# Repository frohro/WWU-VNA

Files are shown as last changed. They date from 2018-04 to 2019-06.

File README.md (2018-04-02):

# WWU-VNA
An Inexpensive Vector Network Analyzer Project for the Walla Walla University Electronics II Class

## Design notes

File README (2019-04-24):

This is some source code for the WWU VNA.  The hardware files can be found at this repository:  
https://github.com/frohro/WWU-VNA

These instructions were done an a Ubuntu Linux computer.  They will vary slightly for Windows or OS X.

Build Instructions:

	- git clone the repository.  
	- Install Code Composer Studio. (This works with CCS 8.2 and 9.0.) 
		- You need the MSP432 Red board library version 5.23.1 or later or you will have build errors.
	- Install Energia, and using Energia's Tools->Boards:->Boards Manager, add the MSP432P401P (red board)
	- Energia uses the Arduino way of handling libraries, and it is easiest to use that as well, because
		CCS knows how to import things better that way.  So in your ~/Energia/libraries folder make 
		folders for each of the libraries.  Mine look like this.
		:~/Energia$ ls -lah libraries
		total 36K
		drwxr-xr-x 8 frohro frohro 4.0K Apr 15 21:07 .
		drwxr-xr-x 5 frohro frohro 4.0K Apr  5 14:30 ..
		drwxr-xr-x 2 frohro frohro 4.0K Apr 21 21:29 adc14vna
		drwxr-xr-x 2 frohro frohro 4.0K Apr 15 21:15 constants
		drwxr-xr-x 2 frohro frohro 4.0K Apr  5 14:33 DynamicCommandParser
		-rw-r--r-- 1 frohro frohro   88 Oct 11  2018 readme.txt
		drwxr-xr-x 2 frohro frohro 4.0K Apr 21 21:31 si5351
		drwxr-xr-x 2 frohro frohro 4.0K Apr 21 21:30 SignalProcessing
		
		Inside those make symbolic links to the appropriate files in your git repository.
		For example, 

	- Import Energia Sketch using File->Import...->Energia->Energia Sketch.
	- Be sure to select MSP432P401R as the processor.
	- Right click on the project, and select add files.
		- Add the .cpp, .c, and .h files.
	- Click the hammer to build in CCS.

	- Under languages, select C11 and c++17
	- Under Build Settings->Miscellaneous->Miscellaneous C++ source specific flags add -fpermissive.

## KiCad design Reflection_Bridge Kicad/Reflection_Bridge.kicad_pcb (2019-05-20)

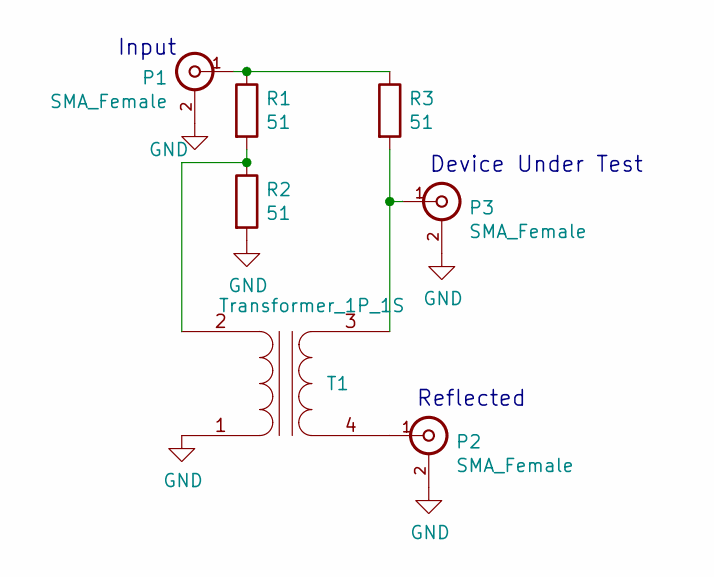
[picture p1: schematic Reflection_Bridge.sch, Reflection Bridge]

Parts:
P1, P2, P3: SMA_Female; SMA_EDGE
R1, R2, R3: 51; R_0805
T1: Transformer_1P_1S; 1_to_1_Balun

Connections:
GND: P1.2 (Ext), P2.2 (Ext), P3.2 (Ext), R2.2, T1.1 (AA)
unnamed: P1.1 (In), R1.1, R3.1
unnamed: P2.1 (In), T1.4 (SB)
unnamed: P3.1 (In), R3.2, T1.3 (SA)
unnamed: R1.2, R2.1, T1.2 (AB)

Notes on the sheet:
Input
Device Under Test
Reflected

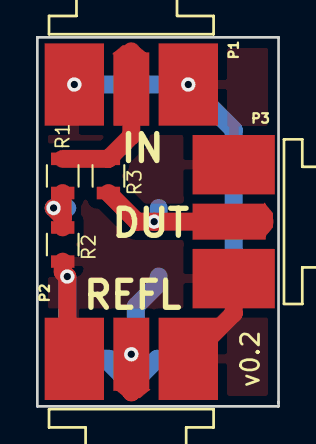
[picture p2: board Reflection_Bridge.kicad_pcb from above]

Board: 2 copper layers, 13.4 x 20.5 mm, 7 parts (1 on the bottom side), 5 nets.

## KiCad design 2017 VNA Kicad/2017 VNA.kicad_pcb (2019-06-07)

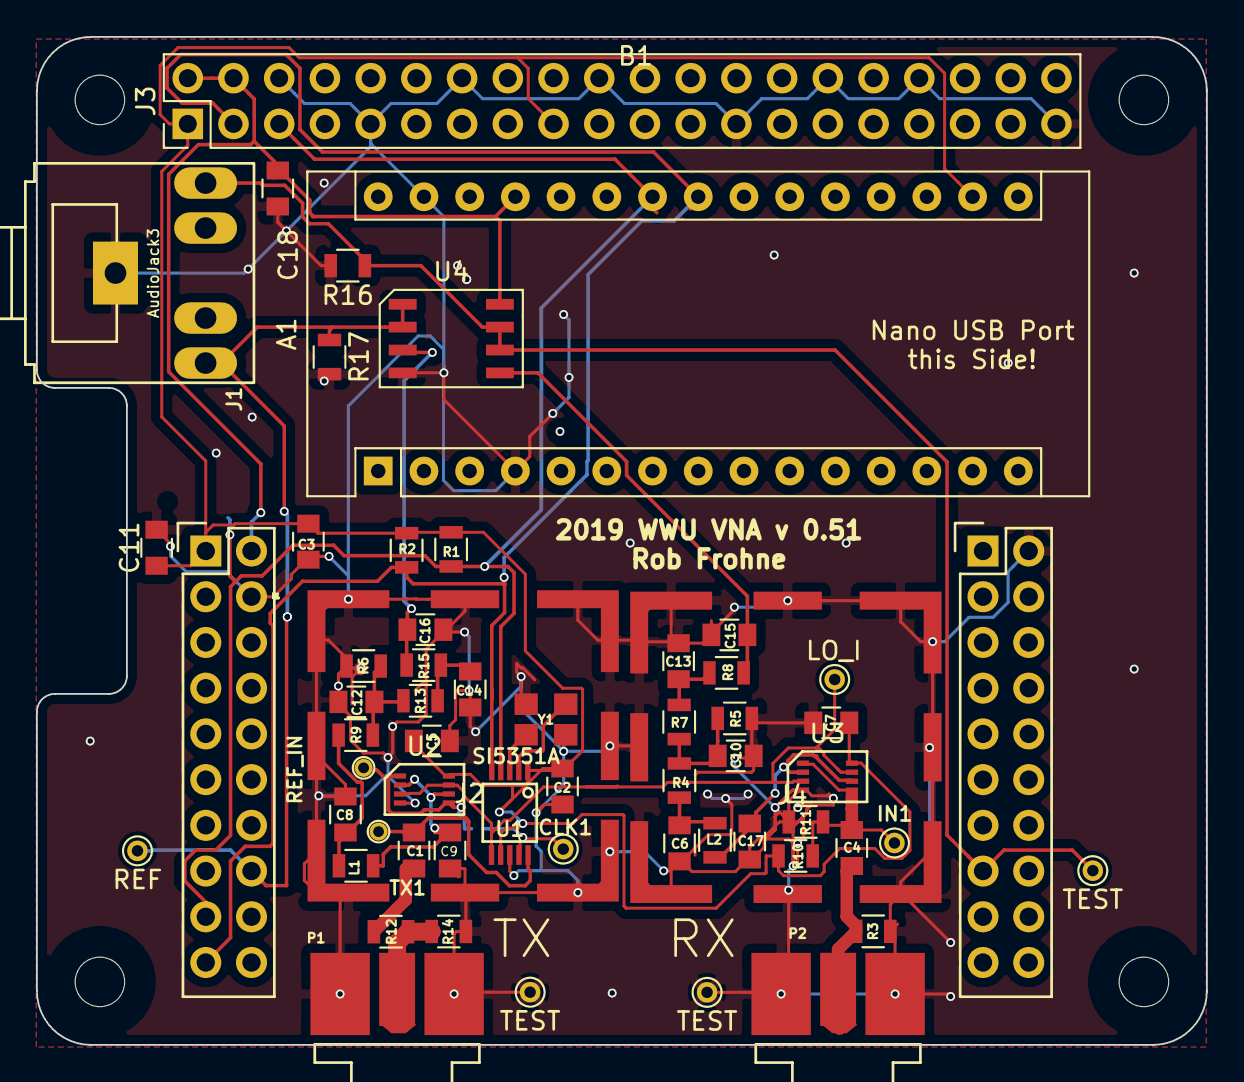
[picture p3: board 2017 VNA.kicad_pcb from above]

Board: 2 copper layers, 65.0 x 56.0 mm, 60 parts (1 on the bottom side), 27 nets.

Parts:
A1: Arduino_Nano_v3.x; Arduino_Nano
B1: EXP-_MSP432P401R_BoosterPack; TI_BoosterPack
C1, C4: 1.0uF; C_0805
C2: .1uf; C_0805
C3: 10uF; C_0805
C5, C7: .1uF; C_0805
C6, C8: 680nF; C_0805
C9, C17: .005uF; C_0805
C10, C12: 10nF; C_0805
C11, C18: 0.1uF; C_0805
C13, C14, C15, C16: 1nF; C_0805
CLK1: LO_Q; PINTST
GND1, GND2: TEST; PINTST
IN1: IN; PINTST
J1: AudioJack3; Tayda_3.5mm_stereo_TRS_jack_A-853
J2, J4: RF_Shield_Two_Pieces; LAIRD-BMI-S-202
J3: Raspberry_Pi_2_3; Pin_Header_Straight_2x20_Pitch2.54mm
JP1: Jumper; SOLDER_JUMPER
L1, L2: 100uH; L_0805
LO_I1: LO_I; PINTST
P1: Output; SMA_EDGE
P2: Input; SMA_EDGE
R1, R2: 4.7k; R_0805
R3: 47; R_0805
R4, R9: 10k; R_0805
R5, R6: 30k; R_0805
R7, R13: 51k; R_0805
R8, R15: 1M; R_0805
R10: 39K; R_0805
R11: 220K; R_0805
R12, R14: R; R_0805
R16, R17: 180; R_0805
TP1: REF_IN; PINTST
TP2: REF; PINTST
TP3: TEST; PINTST
TX1: LO_Q; PINTST
U1: SI5351A; MSOP-10
U2, U3: NL7WB66; VFSOP-8
U4: LM2904; SOIC-8
Y1: CX3225

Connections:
+3V3: A1.17, B1.3.3V, C2.2, C3.1, C5.2, C7.1, C11.1, J3.1, J3.17, R1.2, R2.2, R10.1, U1.1, U1.7, U2.8, U3.8
+5V: A1.27, B1.5V, C18.1, J3.2, J3.4, U4.8
/LO_I: LO_I1.1, U1.6, U2.3, U2.7, U3.3, U3.7
/Ref_In: JP1.2, TP1.1, U2.1, U2.5
/SCL: A1.24, B1.P6.5, J3.5, R1.1, U1.4
/SDA: A1.23, B1.P6.4, J3.3, R2.1, U1.5
/TX: C1.2, TX1.1, U1.10
/Test_In: C4.1, IN1.1, R10.2, R11.1, U3.1, U3.5
GND: A1.4, A1.29, B1.GND, B1.GND1, C2.1, C3.2, C5.1, C6.2, C7.2, C8.2, C9.2, C10.2, C11.2, C12.2, C13.2, C14.2, C15.2, C16.2, C17.2, C18.2, GND1.1, GND2.1, J1.1, J2.1, J3.6, J3.9, J3.14, J3.20, J3.25, J3.30, J3.34, J3.39, J4.1, P1.2, P2.2, R3.2, R5.2, R6.2, R11.2, R14.1, R16.2, R17.2, U1.8, U2.4, U3.4, U4.4, Y1.2, Y1.4
unnamed: B1.P4.7, J1.3, R17.1, TP2.1, U4.1, U4.2
unnamed: B1.P5.1, J1.2, R16.1, TP3.1, U4.6, U4.7
unnamed: C1.1, R12.2
unnamed: C4.2, P2.1, R3.1
unnamed: C6.1, L2.2, R4.2
unnamed: C8.1, L1.2, R9.2
unnamed: C9.1, L1.1, U2.2, U2.6
unnamed: C10.1, R4.1, R5.1, R7.2
unnamed: C12.1, R6.1, R9.1, R13.2
unnamed: C13.1, R7.1, R8.2
unnamed: C14.1, R13.1, R15.2
unnamed: C15.1, R8.1, U4.5
unnamed: C16.1, R15.1, U4.3
unnamed: C17.1, L2.1, U3.2, U3.6
unnamed: CLK1.1, JP1.1, U1.9
unnamed: P1.1, R12.1, R14.2
unnamed: U1.2, Y1.1
unnamed: U1.3, Y1.3

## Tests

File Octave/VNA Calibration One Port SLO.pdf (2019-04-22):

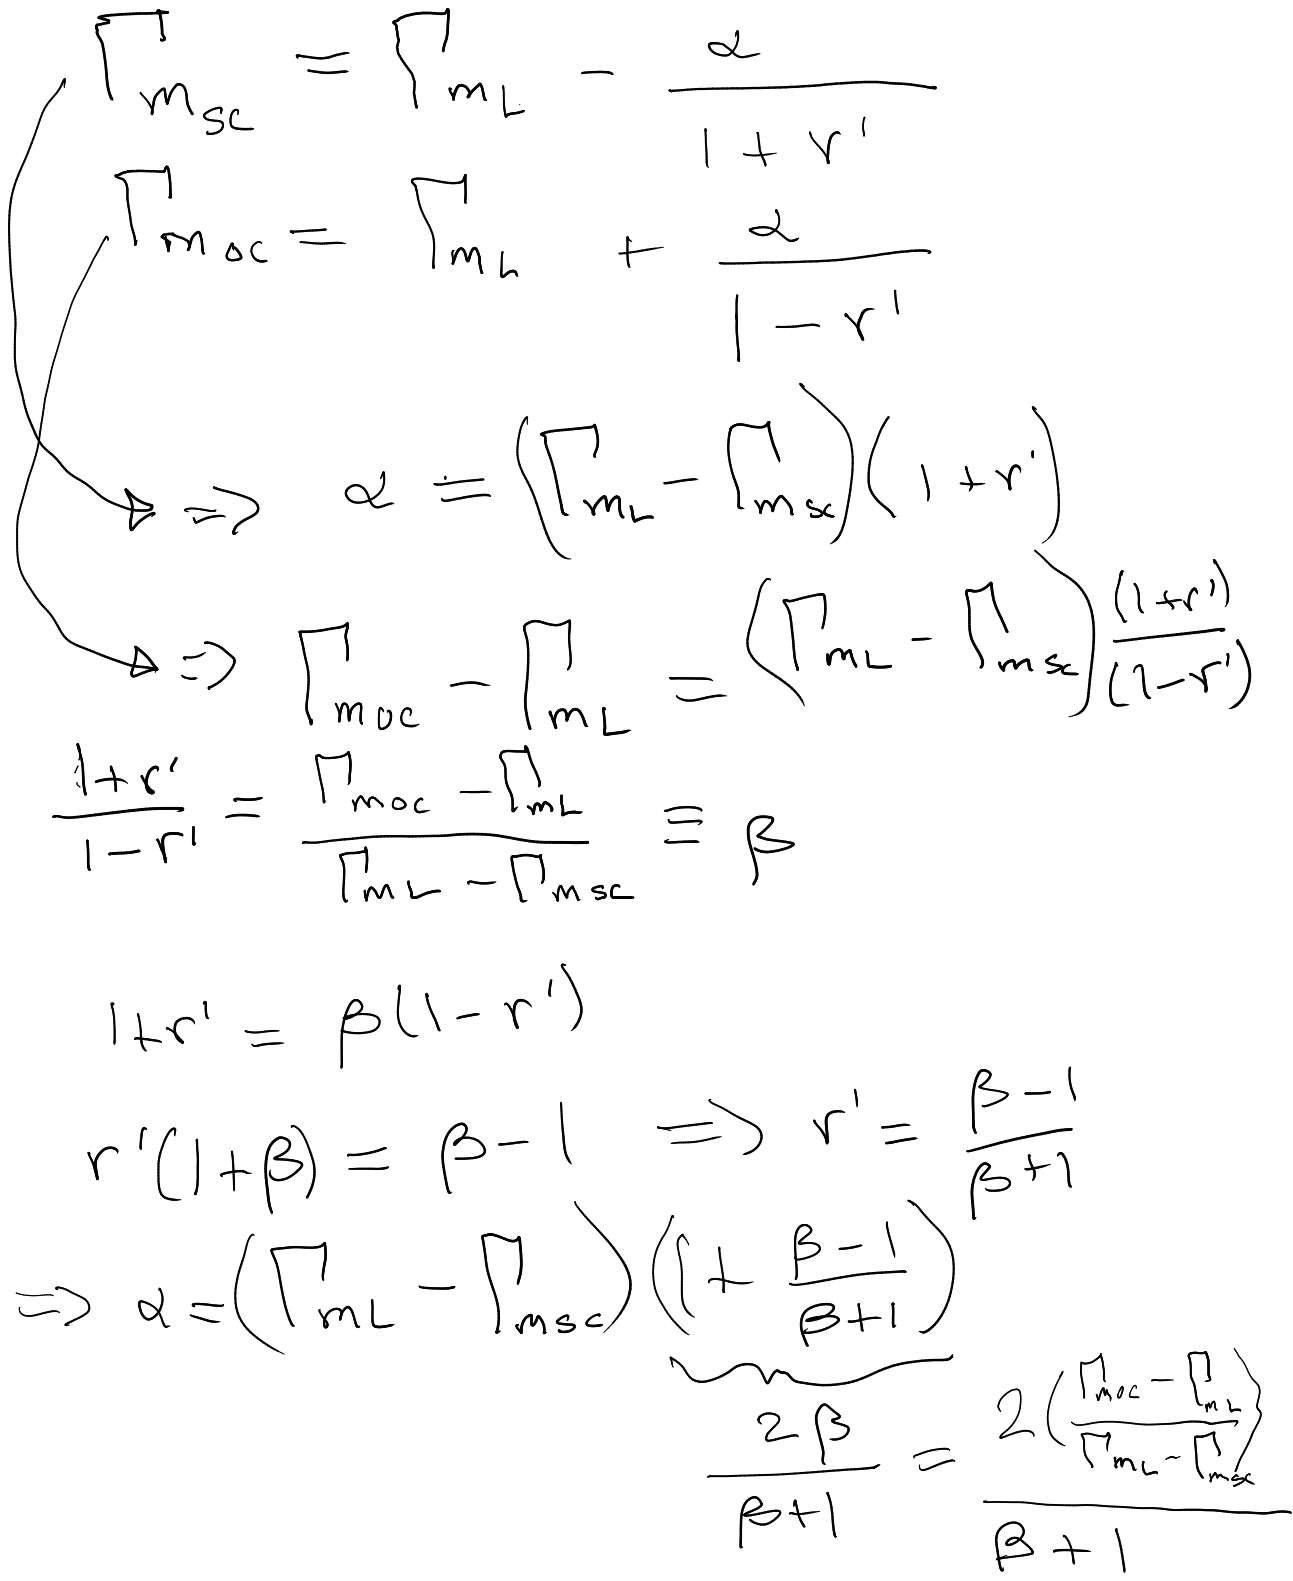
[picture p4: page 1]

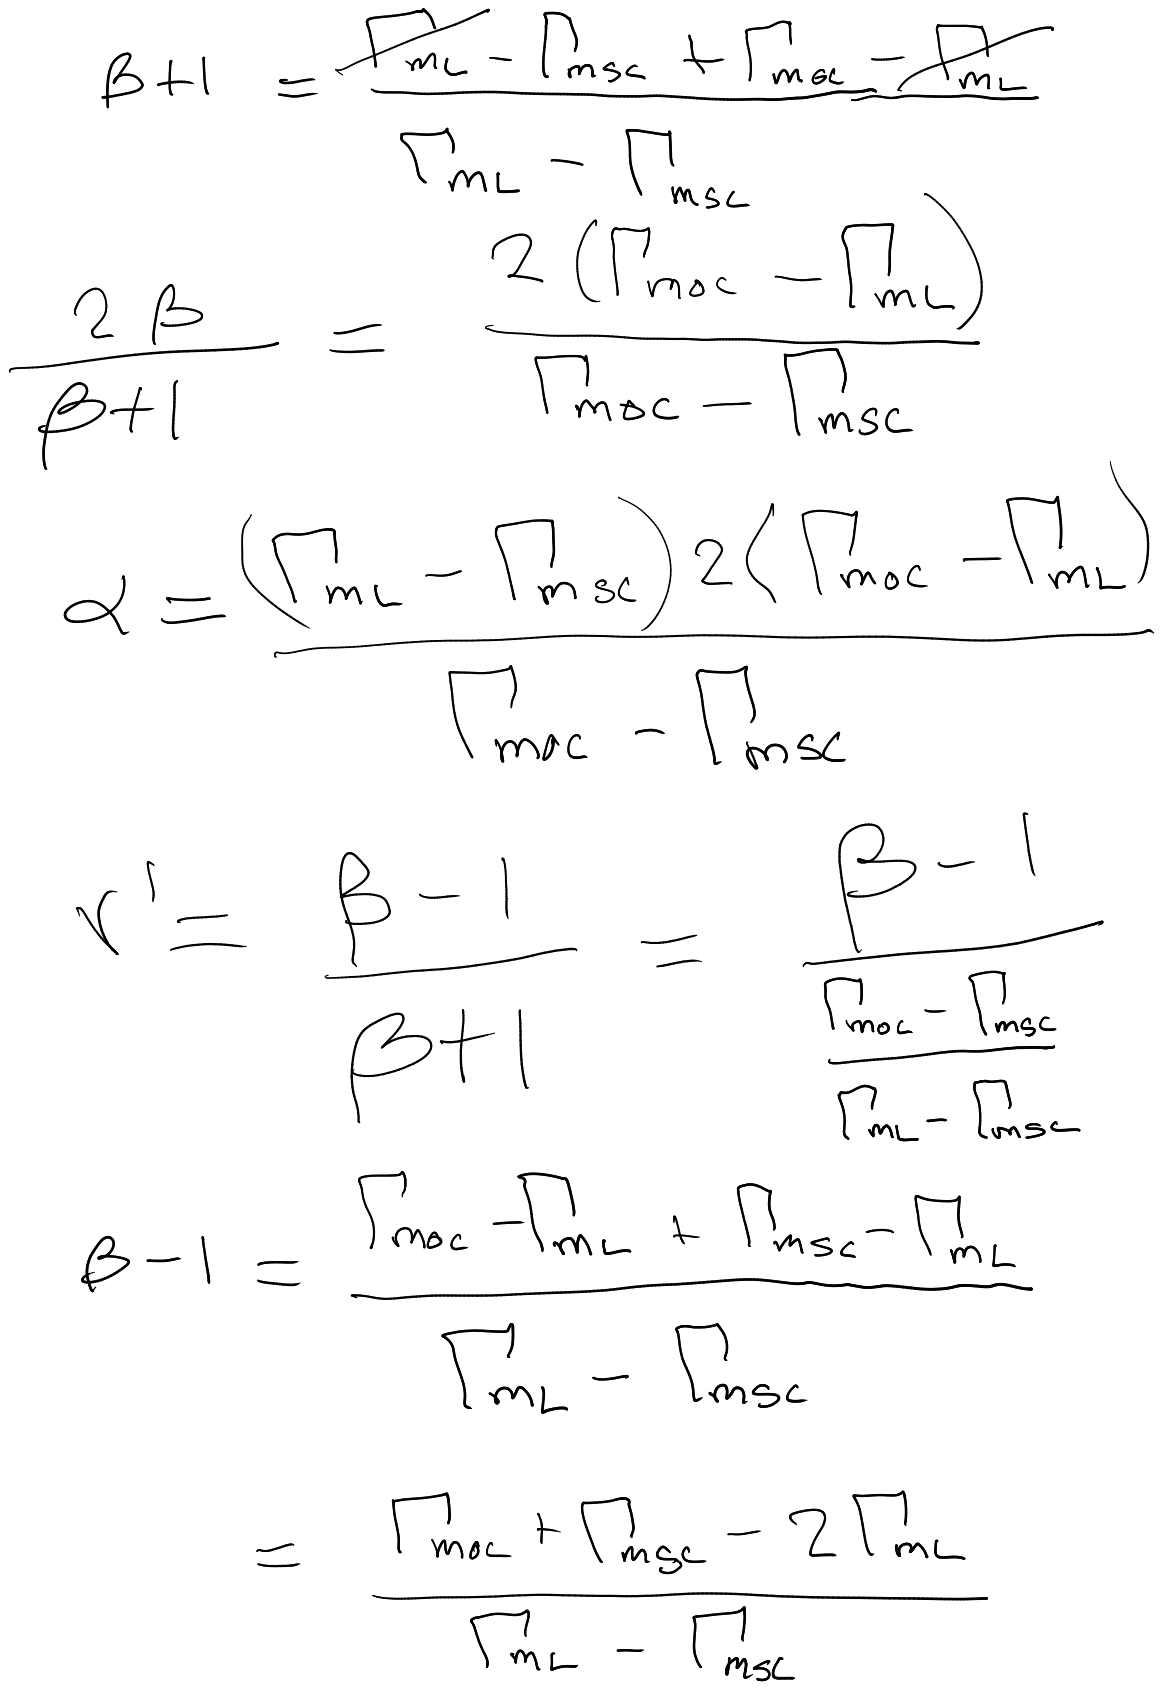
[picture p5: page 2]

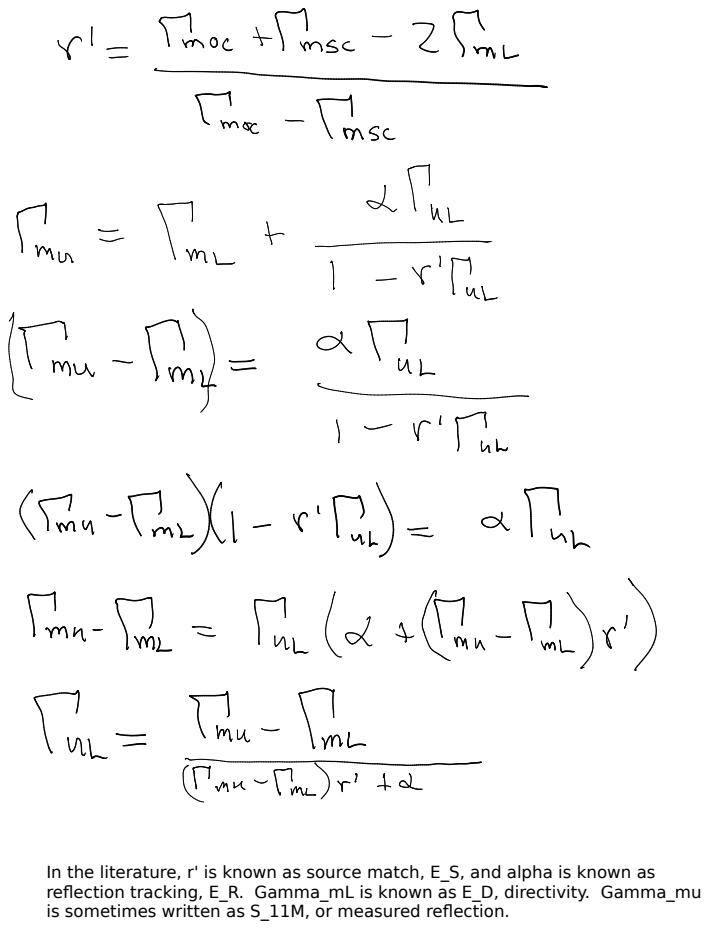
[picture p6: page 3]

In the literature, r' is known as source match, E_S, and alpha is known as
reflection tracking, E_R. Gamma_mL is known as E_D, directivity. Gamma_mu
is sometimes written as S_11M, or measured reflection.

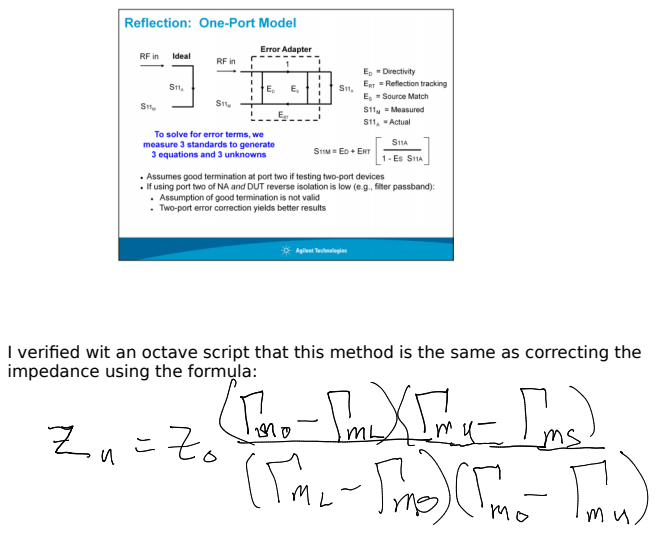
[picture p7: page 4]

I verified wit an octave script that this method is the same as correcting the
impedance using the formula:

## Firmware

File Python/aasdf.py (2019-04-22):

#!/usr/bin/env python3

# Control program for the Red Pitaya vector network analyzer
# Copyright (C) 2017  Pavel Demin
#
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
import sys
import struct
import warnings
import serial

from functools import partial

import numpy as np

import matplotlib
matplotlib.use('Qt5Agg')
from matplotlib.backends.backend_qt5agg import FigureCanvasQTAgg as FigureCanvas
from matplotlib.backends.backend_qt5agg import NavigationToolbar2QT as NavigationToolbar
from matplotlib.figure import Figure
from matplotlib.ticker import Formatter, FuncFormatter

from PyQt5.uic import loadUiType
from PyQt5.QtCore import QRegExp, QTimer, QSettings, QDir, Qt
from PyQt5.QtGui import QRegExpValidator
from PyQt5.QtWidgets import QApplication, QMainWindow, QMessageBox, QDialog, QFileDialog, QPushButton, QLabel, QSpinBox
from PyQt5.QtNetwork import QAbstractSocket, QTcpSocket

Ui_VNA, QMainWindow = loadUiType('vna.ui')

def unicode_minus(s):
  return s.replace('-', '\u2212')

def metric_prefix(x, pos = None):
  if x == 0.0:
    s = '0'
  elif abs(x) >= 1.0e5:
    if x > 0.0:
      s = '99.9k'
    else:
      s = '-99.9k'
  elif abs(x) < 1.0e-2:
    if x > 0.0:
      s = '9.99m'
    else:
      s = '-9.99m'
  elif abs(x) >= 1.0e3:
    s = '%.3gk' % (x * 1.0e-3)
  elif abs(x) >= 1.0e0:
    s = '%.3g' % x
  elif abs(x) >= 1.0e-3:
    s = '%.3gm' % (x * 1e+3)
  else:
    s = '%.3g' % x
  return unicode_minus(s)

class Measurement:
  def __init__(self, start, stop, size):
    self.freq = np.linspace(start, stop, size)
    self.data = np.zeros(size, np.complex64)
    self.period = 62500

class FigureTab:
  cursors = [15000, 45000]
  colors = ['orange', 'violet']

  def __init__(self, layout, vna):
    # create figure
    self.figure = Figure()
    if sys.platform != 'win32':
      self.figure.set_facecolor('none')
    self.canvas = FigureCanvas(self.figure)
    layout.addWidget(self.canvas)
    # create navigation toolbar
    self.toolbar = NavigationToolbar(self.canvas, None, False)
    self.toolbar.layout().setSpacing(6)
    # remove subplots action
    actions = self.toolbar.actions()
    if int(matplotlib.__version__[0]) < 2:
      self.toolbar.removeAction(actions[7])
    else:
      self.toolbar.removeAction(actions[6])
    self.toolbar.addSeparator()
    self.cursorLabels = {}
    self.cursorValues = {}
    self.cursorMarkers = {}
    self.cursorPressed = {}
    for i in range(len(self.cursors)):
      self.cursorMarkers[i] = None
      self.cursorPressed[i] = False
      self.cursorLabels[i] = QLabel('Cursor %d, kHz' % (i + 1))
      self.cursorLabels[i].setStyleSheet('color: %s' % self.colors[i])
      self.cursorValues[i] = QSpinBox()
      self.cursorValues[i].setMinimumSize(90, 0)
      self.cursorValues[i].setSingleStep(10)
      self.cursorValues[i].setAlignment(Qt.AlignRight | Qt.AlignTrailing | Qt.AlignVCenter)
      self.toolbar.addWidget(self.cursorLabels[i])
      self.toolbar.addWidget(self.cursorValues[i])
      self.cursorValues[i].valueChanged.connect(partial(self.set_cursor, i))
      self.canvas.mpl_connect('button_press_event', partial(self.press_marker, i))
      self.canvas.mpl_connect('motion_notify_event', partial(self.move_marker, i))
      self.canvas.mpl_connect('button_release_event', partial(self.release_marker, i))
    self.toolbar.addSeparator()
    self.plotButton = QPushButton('Rescale')
    self.toolbar.addWidget(self.plotButton)
    layout.addWidget(self.toolbar)
    self.plotButton.clicked.connect(self.plot)
    self.mode = None
    self.vna = vna

  def add_cursors(self, axes):
    if self.mode == 'gain_short' or self.mode == 'gain_open':
      columns = ['Freq., kHz', 'G, dB', r'$\angle$ G, deg']
    else:
      columns = ['Freq., kHz', 'Re(Z), \u03A9', 'Im(Z), \u03A9', '|Z|, \u03A9', r'$\angle$ Z, deg', 'SWR', r'|$\Gamma$|', r'$\angle$ $\Gamma$, deg', 'RL, dB']
    y = len(self.cursors) * 0.04 + 0.01
    for i in range(len(columns)):
      self.figure.text(0.19 + 0.1 * i, y, columns[i], horizontalalignment = 'right')
    self.cursorRows = {}
    for i in range(len(self.cursors)):
      y = len(self.cursors) * 0.04 - 0.03 - 0.04 * i
      self.figure.text(0.01, y, 'Cursor %d' % (i + 1), color = self.colors[i])
      self.cursorRows[i] = {}
      for j in range(len(columns)):
        self.cursorRows[i][j] = self.figure.text(0.19 + 0.1 * j, y, '', horizontalalignment = 'right')
      if self.mode == 'smith':
        self.cursorMarkers[i], = axes.plot(0.0, 0.0, marker = 'o', color = self.colors[i])
      else:
        self.cursorMarkers[i] = axes.axvline(0.0, color = self.colors[i], linewidth = 2)
      self.set_cursor(i, self.cursorValues[i].value())

  def set_cursor(self, index, value):
    FigureTab.cursors[index] = value
    marker = self.cursorMarkers[index]
    if marker is None: return
    row = self.cursorRows[index]
    freq = value
    gamma = self.vna.gamma(freq)
    if self.mode == 'smith':
      marker.set_xdata(gamma.real)
      marker.set_ydata(gamma.imag)
    else:
      marker.set_xdata(freq)
    row[0].set_text('%d' % freq)
    if self.mode == 'gain_short':
      gain = self.vna.gain_short(freq)
      magnitude = 20.0 * np.log10(np.absolute(gain))
      angle = np.angle(gain, deg = True)
      row[1].set_text(unicode_minus('%.1f' % magnitude))
      row[2].set_text(unicode_minus('%.1f' % angle))
    elif self.mode == 'gain_open':
      gain = self.vna.gain_open(freq)
      magnitude = 20.0 * np.log10(np.absolute(gain))
      angle = np.angle(gain, deg = True)
      row[1].set_text(unicode_minus('%.1f' % magnitude))
      row[2].set_text(unicode_minus('%.1f' % angle))
    else:
      swr = self.vna.swr(freq)
      z = self.vna.impedance(freq)
      rl = 20.0 * np.log10(np.absolute(gamma))
      if rl > -0.01: rl = 0.0
      row[1].set_text(metric_prefix(z.real))
      row[2].set_text(metric_prefix(z.imag))
      row[3].set_text(metric_prefix(np.absolute(z)))
      angle = np.angle(z, deg = True)
      if np.abs(angle) < 0.1: angle = 0.0
      row[4].set_text(unicode_minus('%.1f' % angle))
      row[5].set_text(unicode_minus('%.2f' % swr))
      row[6].set_text(unicode_minus('%.2f' % np.absolute(gamma)))
      angle = np.angle(gamma, deg = True)
      if np.abs(angle) < 0.1: angle = 0.0
      row[7].set_text(unicode_minus('%.1f' % angle))
      row[8].set_text(unicode_minus('%.2f' % rl))
    self.canvas.draw()

  def press_marker(self, index, event):
    if not event.inaxes: return
    if self.mode == 'smith': return
    marker = self.cursorMarkers[index]
    if marker is None: return
    contains, misc = marker.contains(event)
    if not contains: return
    self.cursorPressed[index] = True

  def move_marker(self, index, event):
    if not event.inaxes: return
    if self.mode == 'smith': return
    if not self.cursorPressed[index]: return
    self.cursorValues[index].setValue(event.xdata)

  def release_marker(self, index, event):
    self.cursorPressed[index] = False

  def xlim(self, freq):
    start = freq[0]
    stop = freq[-1]
    min = np.minimum(start, stop)
    max = np.maximum(start, stop)
    margin = (max - min) / 50
    return (min - margin, max + margin)

  def plot(self):
    getattr(self, 'plot_%s' % self.mode)()

  def update(self, mode):
    start = self.vna.dut.freq[0]
    stop = self.vna.dut.freq[-1]
    min = np.minimum(start, stop)
    max = np.maximum(start, stop)
    for i in range(len(self.cursors)):
      value = self.cursors[i]
      self.cursorValues[i].setRange(min, max)
      self.cursorValues[i].setValue(value)
      self.set_cursor(i, value)
    getattr(self, 'update_%s' % mode)()

  def plot_curves(self, freq, data1, label1, limit1, data2, label2, limit2):
    matplotlib.rcdefaults()
    matplotlib.rcParams['axes.formatter.use_mathtext'] = True
    self.figure.clf()
    bottom = len(self.cursors) * 0.04 + 0.13
    self.figure.subplots_adjust(left = 0.16, bottom = bottom, right = 0.84, top = 0.96)
    axes1 = self.figure.add_subplot(111)
    axes1.cla()
    axes1.xaxis.grid()
    axes1.set_xlabel('kHz')
    axes1.set_ylabel(label1)
    xlim = self.xlim(freq)
    axes1.set_xlim(xlim)
    if limit1 is not None: axes1.set_ylim(limit1)
    self.curve1, = axes1.plot(freq, data1, color = 'blue', label = label1)
    self.add_cursors(axes1)
    if data2 is None:
      self.canvas.draw()
      return
    axes1.tick_params('y', color = 'blue', labelcolor = 'blue')
    axes1.yaxis.label.set_color('blue')
    axes2 = axes1.twinx()
    axes2.spines['left'].set_color('blue')
    axes2.spines['right'].set_color('red')
    axes2.set_ylabel(label2)
    axes2.set_xlim(xlim)
    if limit2 is not None: axes2.set_ylim(limit2)
    axes2.tick_params('y', color = 'red', labelcolor = 'red')
    axes2.yaxis.label.set_color('red')
    self.curve2, = axes2.plot(freq, data2, color = 'red', label = label2)
    self.canvas.draw()

  def plot_gain(self, gain):
    freq = self.vna.dut.freq
    data1 = 20.0 * np.log10(np.absolute(gain))
    data2 = np.angle(gain, deg = True)
    self.plot_curves(freq, data1, 'G, dB', (-110, 110.0), data2, r'$\angle$ G, deg', (-198, 198))

  def plot_gain_short(self):
    self.mode = 'gain_short'
    self.plot_gain(self.vna.gain_short(self.vna.dut.freq))

  def plot_gain_open(self):
    self.mode = 'gain_open'
    self.plot_gain(self.vna.gain_open(self.vna.dut.freq))

  def update_gain(self, gain, mode):
    if self.mode == mode:
      self.curve1.set_xdata(self.vna.dut.freq)
      self.curve1.set_ydata(20.0 * np.log10(np.absolute(gain)))
      self.curve2.set_xdata(self.vna.dut.freq)
      self.curve2.set_ydata(np.angle(gain, deg = True))
      self.canvas.draw()
    else:
      self.mode = mode
      self.plot_gain(gain)

  def update_gain_short(self):
    self.update_gain(self.vna.gain_short(self.vna.dut.freq), 'gain_short')

  def update_gain_open(self):
    self.update_gain(self.vna.gain_open(self.vna.dut.freq), 'gain_open')

  def plot_magphase(self, freq, data, label, mode):
    self.mode = mode
    data1 = np.absolute(data)
    data2 = np.angle(data, deg = True)
    max = np.fmax(0.01, data1.max())
    label1 = r'|%s|' % label
    label2 = r'$\angle$ %s, deg' % label
    self.plot_curves(freq, data1, label1, (-0.05 * max, 1.05 * max), data2, label2, (-198, 198))

  def update_magphase(self, freq, data, label, mode):
    if self.mode == mode:
      self.curve1.set_xdata(freq)
      self.curve1.set_ydata(np.absolute(data))
      self.curve2.set_xdata(freq)
      self.curve2.set_ydata(np.angle(data, deg = True))
      self.canvas.draw()
    else:
      self.plot_magphase(freq, data, label, mode)

  def plot_open(self):
    self.plot_magphase(self.vna.open.freq, self.vna.open.data, 'open', 'open')

  def update_open(self):
    self.update_magphase(self.vna.open.freq, self.vna.open.data, 'open', 'open')

  def plot_short(self):
    self.plot_magphase(self.vna.short.freq, self.vna.short.data, 'short', 'short')

  def update_short(self):
    self.update_magphase(self.vna.short.freq, self.vna.short.data, 'short', 'short')

  def plot_load(self):
    self.plot_magphase(self.vna.load.freq, self.vna.load.data, 'load', 'load')

  def update_load(self):
    self.update_magphase(self.vna.load.freq, self.vna.load.data, 'load', 'load')

  def plot_dut(self):
    self.plot_magphase(self.vna.dut.freq, self.vna.dut.data, 'dut', 'dut')

  def update_dut(self):
    self.update_magphase(self.vna.dut.freq, self.vna.dut.data, 'dut', 'dut')
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

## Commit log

2017-12-31 Updating to work with the latest PCB (version 0.3).
2018-04-02 Initial Commit
    I am starting a repository for the WWU Vector Network Analyzer generally. In the past, I have shared software on github, but this will have the hardware design files as well as the software.
    [2017 VNA.kicad_pcb, 2017 VNA.sch]
2018-04-03 fixed library files
    [2017 VNA.sch]
2018-04-03 fixed some test point libraries
    [2017 VNA.sch]
2018-04-03 Added note about R3.
    R3 added after PCB was manufactured.
    [2017 VNA.sch]
2018-04-03 fixed a few more lib values
    [2017 VNA.sch]
2018-04-03 added note on R3 (added after PCB made)
    [2017 VNA.sch]
2018-04-04 Added reflection bridge hardware design files
    [Reflection_Bridge-2018-04-04-16-37-06.sch, Reflection_Bridge-B.Cu.gbr, Reflection_Bridge-B.Mask.gbr, Reflection_Bridge-B.Paste.gbr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]
2018-04-17 updated the LTSpice files and fixed a bug with C12 (wrong value).
    [2017 VNA.sch]
2018-04-18 Updated the Si5351a library, and calibrated my oscillator.
2018-04-18 Undo fix in case it blows oscillators.
2018-04-19 Fixed the si5351a library prblem by using 2.0.6, and changing the set_correction function to one argument. Octave starts indexing at 1 instead of 0, so fixed that. Fixed the bug in octave script that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
2018-04-24 Fix some printing errors, and change phase to be in degrees. Also add a custom frequency entering.
2018-04-25 Go back to getting the sample frequency from the board.
2018-04-26 New filter idea in progress, and a needed .gitignore for LTSpice-Simulations folder
2018-04-26 Make the new filter realistic
2018-04-26 Improvements to the new filter.
2018-04-28 added dakiry's low pass filter design without inductor
2018-05-29 Fixed the master branch with the emblem and test libs.
    [2017 VNA.sch]
2018-06-05 Changet the IF to 155 Hz, and the octave script serial_test_time.m to match.
2018-06-08 Revert testime.py because it got broken. Also ignore measurements while device is getting to steady state.
2018-06-08 Add hanning window in the python script and make the harmonics print out again in the serial_test_time script
2018-12-06 Adding to README for CCSv8.2, and making compatible with Kicad v5.
    [2017 VNA.kicad_pcb, 2017 VNA.sch, Reflection_Bridge.kicad_pcb]
2018-12-07 A whole lot of things working now - Update to CCS 8.2 - fix DMA to get rid of inflection at beginning - compute the first harmonic on the board and send it back with the COMPUTE command. - Create FIR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
2018-12-09 The commit that fixes everything.
    - Found bug in python script where wrong size hanning window was generated
    - What do you get when you cross an idiot with a small math mistake? 6 months of wondering what the problem was.
    - Added script to compare math being done on board to a library that we have some faith in.
    - Added minus sign to the imaginary filter part becuase I forgot it becuase I'm an idiot.
2018-12-18 Increased the drive to 8mA again.
2018-12-20 Added isolation calibration. It improved isolation 20-30 dB.
2019-02-11 version 5 hardware design (more isolation between channels)
    [2017 VNA.kicad_pcb, 2017 VNA.sch]
2019-02-12 Cosmetic cleanup.
    [2017 VNA.kicad_pcb]
2019-02-21 Moved pin assignments for v 0.5.
2019-03-20 Making sure it is up to date.
    [2017 VNA.kicad_pcb]
2019-04-30 Added notes to fix T1 footprint on the reflection bridge.
    [Reflection_Bridge.kicad_pcb, Reflection_Bridge.sch]
2019-05-07 Added octave script to use soundcard.
    [2017 VNA.sch]
2019-05-15 New PCB spin.
    [2017 VNA.kicad_pcb, 2017 VNA.sch]
2019-05-15 Added the buffer stage and ADC for MSP432 it the LTspice simulation.
2019-05-16 Added v0.2 of reflection bridge.
    [Reflection_Bridge.kicad_pcb, Reflection_Bridge.sch]
2019-05-16 Added the footprint for the 3.5mm connector.
    [2017 VNA.kicad_pcb, 2017 VNA.sch]
2019-05-17 Added v0.51 to the Kicad directory.
    [2017 VNA.kicad_pcb]
2019-05-20 Hwi interrupt header testing....
    [2017 VNA.kicad_pcb, 2017 VNA.sch, Reflection_Bridge.kicad_pcb]
2019-06-03 updated the pcb...
    [2017 VNA.kicad_pcb]
2019-06-04 Added some arduino python test scripts.
2019-06-07 Added 180 ohms to bias the emitter follower on the LM2094.
    [2017 VNA.sch]
2019-06-07 Updated the netlest and PCB for v0.52 (180 ohm current sink).
    [2017 VNA.kicad_pcb, 2017 VNA.sch]
2019-06-10 Added vna2019.asc to the LTspice simulations.
    [2017 VNA.sch]

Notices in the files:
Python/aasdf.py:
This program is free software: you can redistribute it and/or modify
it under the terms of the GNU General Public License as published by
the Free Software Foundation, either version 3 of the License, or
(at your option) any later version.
